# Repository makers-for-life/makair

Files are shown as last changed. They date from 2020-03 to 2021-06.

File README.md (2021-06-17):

MakAir — Covid-19 Ventilator
=====

Mass-producible open-source Covid-19 ARDS ventilator. Aims at helping hospitals cope with a possible shortage of professional ventilators during the outbreak. Worldwide.

**Makair ventilator is the world's first open-source ventilator tested with success on human patients** with ongoing clinical trials in France.

We are a distributed team of 200+ contributors (engineering, medical, regulatory, etc.), mostly spread through France. Makers, developers, university teachers, researchers and medical teams collaborated on this project. Our testing & assembly operations are located in France.

As to ensure international outreach, we made sure that contents required to build your own MakAir ventilator are available in English. The MakAir project has [a website of its own](https://makair.life/).

If you're new there, please read the explanations below. _Your contributions are much welcome!_

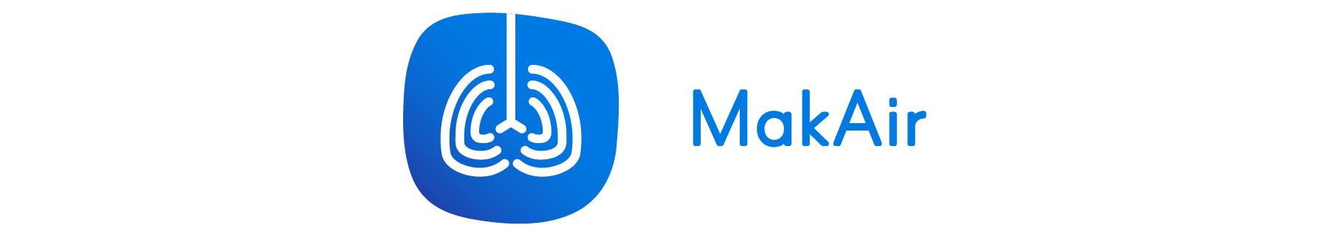
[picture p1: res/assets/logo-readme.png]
MakAir Logo


---

**Quick introduction video:**

<p align="center">
  <a href="https://www.youtube.com/watch?v=3ZcYR6X3NxE">
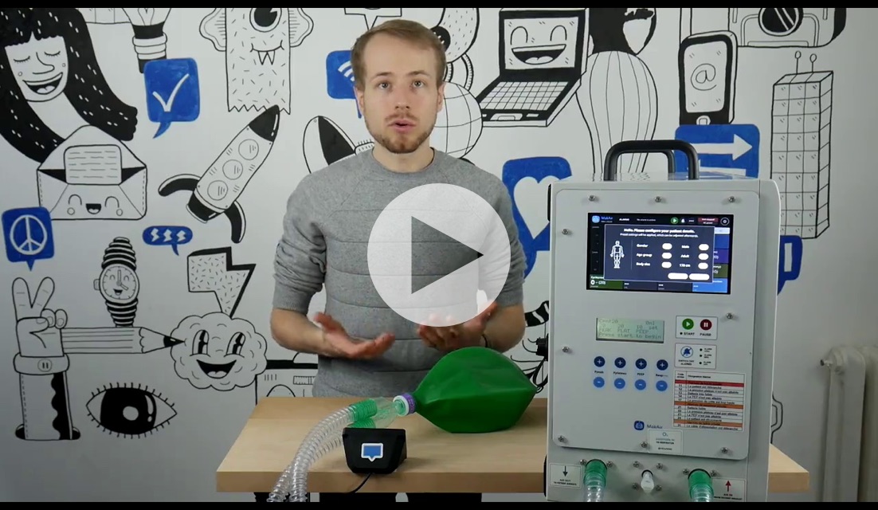
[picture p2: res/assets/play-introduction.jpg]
Play Introduction Video
    
  </a>
</p>

---

# Abstract

Roughly, the idea is as follows: as of April 2020 and due to the Covid-19 pandemic, hospitals throughout the world may start lacking mechanical artificial ventilators. We built a pump, and a valve system (controlled by electronics). This way, the breathing cycle can be enforced by proper air routing through the valve system.

Our ventilator is able to handle pressure-controlled breathing, stabilized using a [PID controller](https://en.wikipedia.org/wiki/PID_controller) in the software.

In order to ensure a proper breathing cycle (inhale + exhale), multiple valves need to be connected together to form a circuit. Their motors need to be controlled in harmony so that the air routing between each valve unit is consistent.

This project provides all the parts required to build a good-enough [ARDS](https://en.wikipedia.org/wiki/Acute_respiratory_distress_syndrome) ventilator from mass-produced components. We provide all the required mechanical parts, electronics designs & boards, and firmwares. This ventilator can be 3D-printed and ran on an Arduino board (the maker way), though we **highly advise** that you work with industrial processes as to mold medical-grade plastic parts and assemble the whole ventilator (this would be required for the built ventilator to pass all medical certifications).

We target a per-unit cost well under 500 EUR, which could easily be shrunk down to 200 EUR or even 100 EUR per ventilator given proper economies of scale, as well as choices of cheaper on-the-shelf components (eg. servomotors).

Features include:

- Pressure controlled ventilation (sedated / intubated patients)
- Volume controlled ventilation (sedated / intubated patients)
- BiPap ventilation (non sedated patients with oxygen mask)
- 4 hours battery life
- Medical-grade alarms
- High flow turbine (up to 100 L/min)
- Up to 15 L/min oxygen
- Fault tolerant design
- Designed to be used continuously and intensively during 30 days

MakAir ventilator has been tested by independent researchers and studies found that it can compare with expensive hospital reanimation ventilators (less than 5% error on target pressures and volumes).

Mechanically-speaking, the overall system is composed of sub-components that can be plugged together and wired to form an air circuit, namely:

- **Air pump** (called "Blower");
- **Air pump casing fit** (called "Blower Holder");
- **Valve system** (called "Pressure Valve");
- **Oxygen Mixer valve** (called "Oxygen Mixer");
- **Air filter casing (patient variant)** (called "Patient Filter Box");
- **Air filter casing (machine variant)** (called "Machine Filter Box"; intake + outtake);
- **Connectors** (called "Pneumatic Connectors");
- **Fan support** (called "Fan Holder");

All those components are fitted in box (ie. a casing) that we designed:

- **Housing container** (called "Casing");

---

# Designs

## MakAir Standard (Current Design)

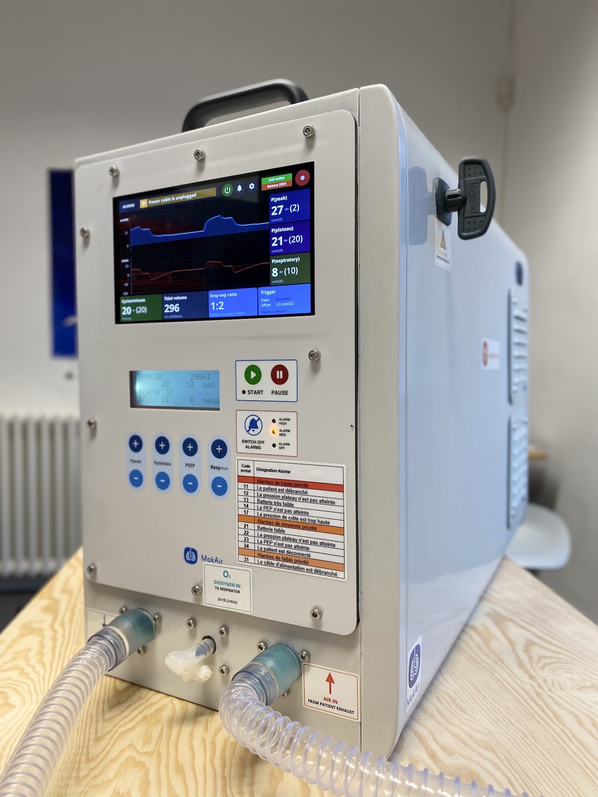
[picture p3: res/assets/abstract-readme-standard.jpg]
MakAir Standard


## MakAir Mini (Experimental Design)

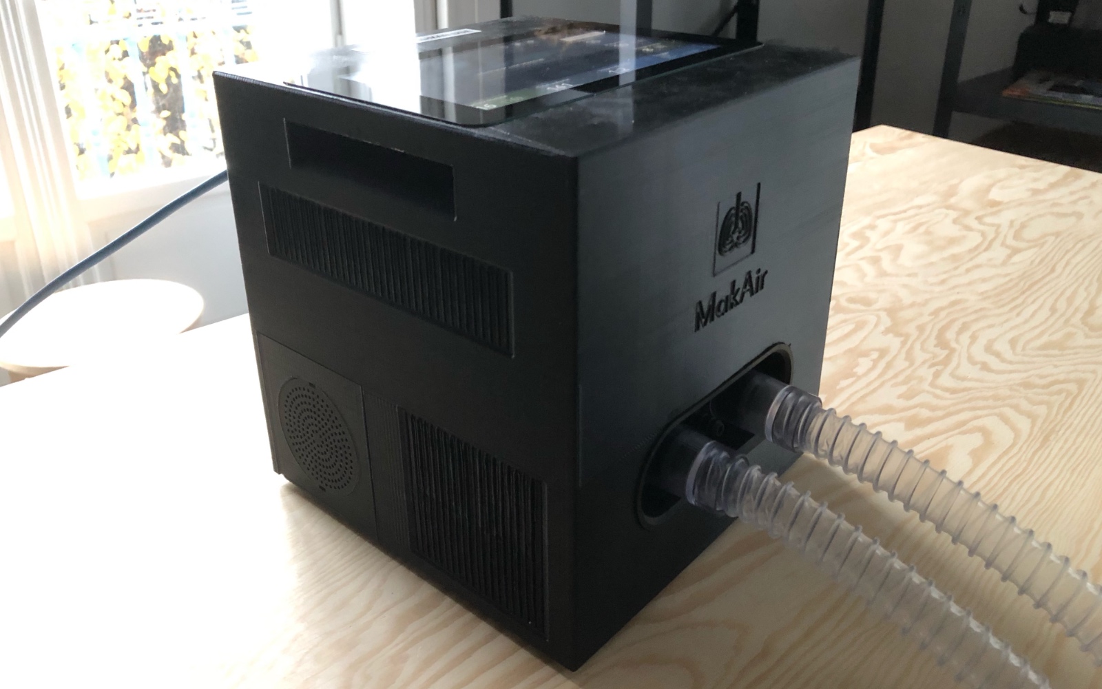
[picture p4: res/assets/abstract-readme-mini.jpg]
MakAir Mini


---

# ⚠️ Warning Notices

**A few important words before you start:**

1. Though 3D-printing (FDM and SLA) can be used to build your own ventilator — this will definitely not scale well to mass-produce MakAir ventilators, and parts might be brittle or leak air. Please work with proper industrial methods and processes if you want to build your own MakAir ventilators.

2. As ARDS patients are sedated, their breathing cycle is forced by mechanical ventilation, while they are intubated. A failing ventilator (due to bad mechanics, pneumatics or software) could kill the patient (O2 desaturation), or permanently damage their lung alveoli (overpressure). It is critical that any self-built MakAir ventilator is tested against a lung simulator system (eg. [ASL 5000](https://www.ingmarmed.com/product/asl-5000-breathing-simulator/)), and validated by medical experts.

3. Medical-grade plastic should be used to produce ventilators, and any kind of grease or adhesive chemicals must be avoided in the ventilator. The ventilators should be produced in a [cleanroom](https://en.wikipedia.org/wiki/Cleanroom) as to avoid dust & germ contaminations.

4. The pneumatic circuit should be thoroughly tested for leaks and its ability to withstand elevated positive air pressure. Joints should be used where relevant, and medical-grade flexible pipes should be used between components.

5. While the MakAir ventilators produced on-site in France were validated by a medical & engineering board, you should independantly seek validation of the MakAir ventilators that you produce; as your assembly methods or parts may vary with ours.

_MakAir and Makers For Life should not be held resposible — at any time, for harm caused to human life (eg. lung damage or loss of life). By building your own MakAir, you are held responsible for its safety validations & use._

# Projects

As the MakAir ventilator project grew up to be quite large, it is split up in sub-repositories (eg. firmware, PCB designs, etc.).

**Software:**

* **[makair-firmware](https://github.com/makers-for-life/makair-firmware)**: The firmware software source code and builds, that runs on the motherboard;
* **[makair-control-ui](https://github.com/makers-for-life/makair-control-ui)**: The control user interface, that shows realtime graphs of the ventilator while running, on a LCD display;
* **[makair-telemetry](https://github.com/makers-for-life/makair-telemetry)**: The telemetry library (and CLI tool), used as a protocol bridge between the Firmware and Control UI;

**Electronics:**

* **[makair-motherboard](https://github.com/makers-for-life/makair-motherboard)**: The motherboard electronics and PCB design;
* **[makair-boards](https://github.com/makers-for-life/makair-boards)**: Other boards PCB design (smaller control boards);

**Mechanics:**

* **[makair-parts](https://github.com/makers-for-life/makair-parts)**: The mechanical parts that can be 3D-printed and assembled to build the pneumatic circuit;
* **[makair-casing](https://github.com/makers-for-life/makair-casing)**: The MakAir casing which houses all electronics and pneumatics;

**Misc.:**

* **[makair-files](https://github.com/makers-for-life/makair-files)**: Large files, eg. the control UI system image that can be readily flashed and used;
* **[makair-simulator](https://github.com/makers-for-life/makair-simulator)**: The MakAir hardware simulator, that let us run a simulated firmware instance on a computer (for development purposes, ie. not used on ventilator units);
* **[makair-simulator-web](https://github.com/makers-for-life/makair-simulator-web)**: The Web version of the MakAir hardware simulator, that let us run a simulated firmware instance in a Web browser (for development purposes, ie. not used on ventilator units);

# How To Build?

This section aims at introducing you on how to manufacture your own MakAir — _the 3D-printed way_. In other words, we will explain there how to build a DIY MakAir using on-the-shelf parts and 3D printers.

## 1️⃣ Print all the parts

In order to 3D-print your MakAir, please first ensure you have access to a [SLS](https://en.wikipedia.org/wiki/Selective_laser_sintering) 3D printer at best (eg. [HP Multi Jet Fusion](https://www8.hp.com/us/en/printers/3d-printers/products/multi-jet-technology.html)), or otherwise a [SLA](https://en.wikipedia.org/wiki/Stereolithography) printer (eg. [Formlabs Form 3](https://formlabs.com/3d-printers/form-3/)). If you want to use a [FDM](https://en.wikipedia.org/wiki/Fused_filament_fabrication) printer (eg. [MakerBot Method](https://www.makerbot.com/3d-printers/method/)), please note that some precise parts have been optimized for SLA or SLS printing. Some parts may not print well using FDM printers, even on decent hardware.

**👉 To sum up:** at best, use a SLS metal printer, else, use a SLA resin printer. If you do not have access to either of these, you may fallback on a FDM filament printer (using [PLA](https://en.wikipedia.org/wiki/Polylactic_acid) or [ABS](https://en.wikipedia.org/wiki/Acrylonitrile_butadiene_styrene) filaments).

### 1. Parts

You can find a list of all parts that should be 3D-printed, as well as the number of parts that should be printed for each one (pick the last active version for each part):

- 1 x **Blower** — Print [all STL parts](https://github.com/makers-for-life/makair-parts/tree/master/src/blower/printing/stl) using the same printer (SLA or SLS; FDM discouraged; 50 microns minimum);
- 2 x **Pressure Valve** — Print [all STL parts](https://github.com/makers-for-life/makair-parts/tree/master/src/pressure-valve/printing/stl) using the same printer (SLA, SLS or FDM; 200 microns minimum);
- 1 x **Oxygen Mixer** — Print [the STL part](https://github.com/makers-for-life/makair-parts/tree/master/src/oxygen-mixer/printing/stl) (SLA or SLS; FDM discouraged; 100 microns minimum);
- 1 x **Patient Filter Box** — Print [all STL parts](https://github.com/makers-for-life/makair-parts/tree/master/src/patient-filter-box/printing/stl) using the same printer (SLA, SLS or FDM; 100 microns minimum);
- 1 x **Machine Filter Box (Intake)** — Print [all STL parts](https://github.com/makers-for-life/makair-parts/tree/master/src/machine-filter-box/printing/stl) using the same printer, make sure that you pick the proper sub-part (SLA or SLS; FDM discouraged; 100 microns minimum);
- 1 x **Machine Filter Box (Outtake)** — Print [all STL parts](https://github.com/makers-for-life/makair-parts/tree/master/src/machine-filter-box/printing/stl) using the same printer, make sure that you pick the proper sub-part (SLA or SLS; FDM discouraged; 100 microns minimum);
- 1 x **Pneumatic Connectors (Blower)** — Print [the STL part](https://github.com/makers-for-life/makair-parts/tree/master/src/pneumatic-connectors/printing/stl) using the same printer, make sure that you pick the proper sub-part (SLA or SLS; FDM discouraged; 100 microns minimum);
- 1 x **Pneumatic Connectors (O2)** — Print [the STL part](https://github.com/makers-for-life/makair-parts/tree/master/src/pneumatic-connectors/printing/stl) using the same printer, make sure that you pick the proper sub-part (SLA or SLS; FDM discouraged; 100 microns minimum);
- 1 x **Pneumatic Connectors (No Pressure)** — Print [the STL part](https://github.com/makers-for-life/makair-parts/tree/master/src/pneumatic-connectors/printing/stl) using the same printer, make sure that you pick the proper sub-part (SLA or SLS; FDM discouraged; 100 microns minimum);
- 1 x **Pneumatic Connectors (Pressure)** — Print [the STL part](https://github.com/makers-for-life/makair-parts/tree/master/src/pneumatic-connectors/printing/stl) using the same printer, make sure that you pick the proper sub-part (SLA or SLS; FDM discouraged; 100 microns minimum);

If you are using your own proprietary blower — _in addition to the parts above_ — please adjust the [Blower Holder](https://github.com/makers-for-life/makair-parts/tree/master/src/blower-holder) CAD model and print it as well (this one prints well using a FDM printer at worst).

### 2. Casing

Now that you got all parts printed, you may assemble them in the MakAir casing box. We recommend that you build the casing using laser-cut acrylic panels. You may find the casing CAD model for [Fusion 360](https://github.com/makers-for-life/makair-casing/tree/master/src/fusion) or as a [STEP file](https://github.com/makers-for-life/makair-casing/tree/master/src/step).

_Please ensure that you cut your acrylic panels using the same sizes than stated on our models; as those sizes are optimized to contain all required parts and electronics in the minimum amount of space._

## 2️⃣ Setup the electronics

Electronics are comprised of two parts: the firmware controller board (typically, an Arduino), and the "raw" PCB electronics (LCD, interface buttons, alarm beeper, etc.). Those parts make up the motherboard, on the top of which a rigid panel is mounted, and user instructions are printed (eg. control button bindings).

### 1. Motherboard

The motherboard electronic schematics and wiring diagrams [can be found there](https://github.com/makers-for-life/makair-motherboard/tree/master/src/schematics). Please pick the last version available.

👋 _If you need help on this step, you may [open an issue](https://github.com/makers-for-life/makair-motherboard/issues/new)._

### 2. Smaller Boards

The smaller boards electronic schematics and wiring diagrams [can be found there](https://github.com/makers-for-life/makair-boards/tree/master/src/schematics). Please pick the last version available. Those boards are used eg. to control the pinch valve motor or Raspberry Pi hardware clock.

👋 _If you need help on this step, you may [open an issue](https://github.com/makers-for-life/makair-boards/issues/new)._

### 3. Control Unit Screen

The control unit is made of a [Raspberry Pi 4](https://www.raspberrypi.org/products/raspberry-pi-4-model-b/) computer, plugged to a [Raspberry Pi Touch Display](https://www.raspberrypi.org/products/raspberry-pi-touch-display/).

👋 _If you need help on this step, you may [open an issue](https://github.com/makers-for-life/makair-control-ui/issues/new)._

## 3️⃣ Flash the firmware

### 1. Ventilator Firmware

Now that both mechanical parts and electronics are ready, you may flash the latest MakAir firmware binary on your firmware controller board (Arduino, ST Nucleo, or other).

Firmware release binaries are available for download on our [releases page](https://github.com/makers-for-life/makair-firmware/releases).

👋 _If you need help on this step, you may [open an issue](https://github.com/makers-for-life/makair-firmware/issues/new)._

### 2. Control Unit Runtime

The Control Unit should be built and ran on the Raspberry Pi 4 using instructions available on the [Control Unit](https://github.com/makers-for-life/makair-control-ui) documentation. You should flash the system image readily available in the [Files](https://github.com/makers-for-life/makair-files) repository.

👋 _If you need help on this step, you may [open an issue](https://github.com/makers-for-life/makair-control-ui/issues/new)._

# Schemes

## Pneumatic Circuit Scheme

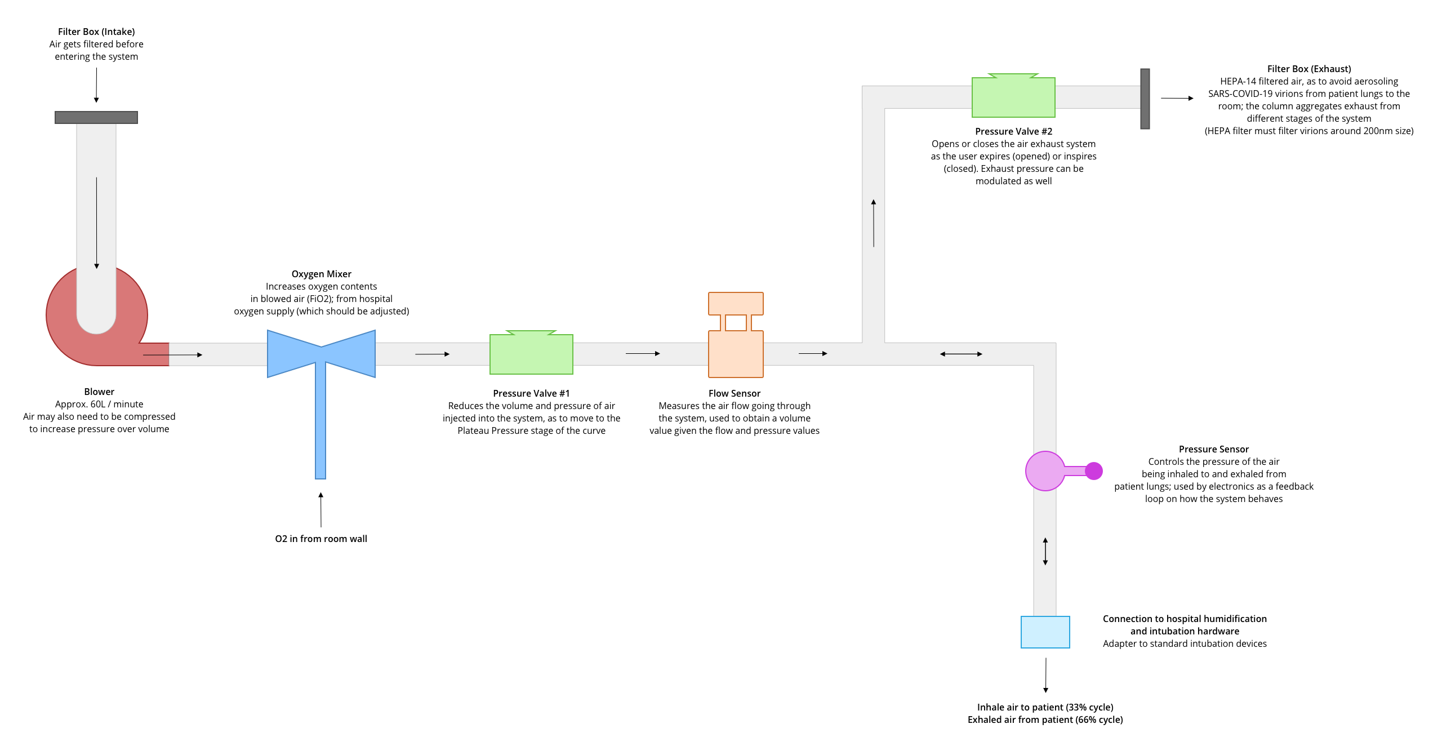
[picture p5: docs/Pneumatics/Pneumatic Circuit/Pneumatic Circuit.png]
Pneumatic Circuit Scheme


_(design by [Valerian Saliou](https://github.com/valeriansaliou))_

## Casing Layout

### Top Part: Electronics (Power & Controllers)

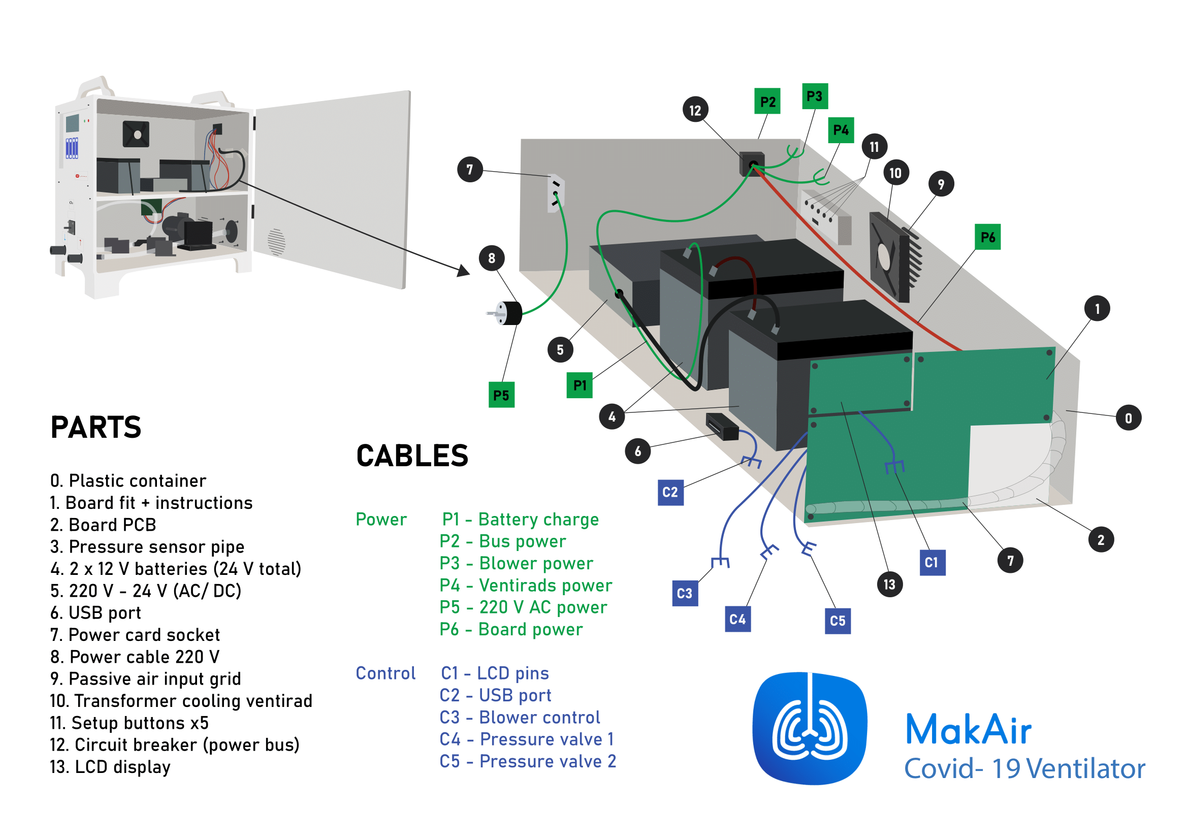
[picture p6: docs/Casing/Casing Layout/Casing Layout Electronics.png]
Casing Layout Electronics Drawing


_(design by Arthur Dagard; drawing by [Valerian Saliou](https://github.com/valeriansaliou); remake by [Lāsma Fedotova](https://github.com/lasmafedotova))_

### Bottom Part: Pneumatics

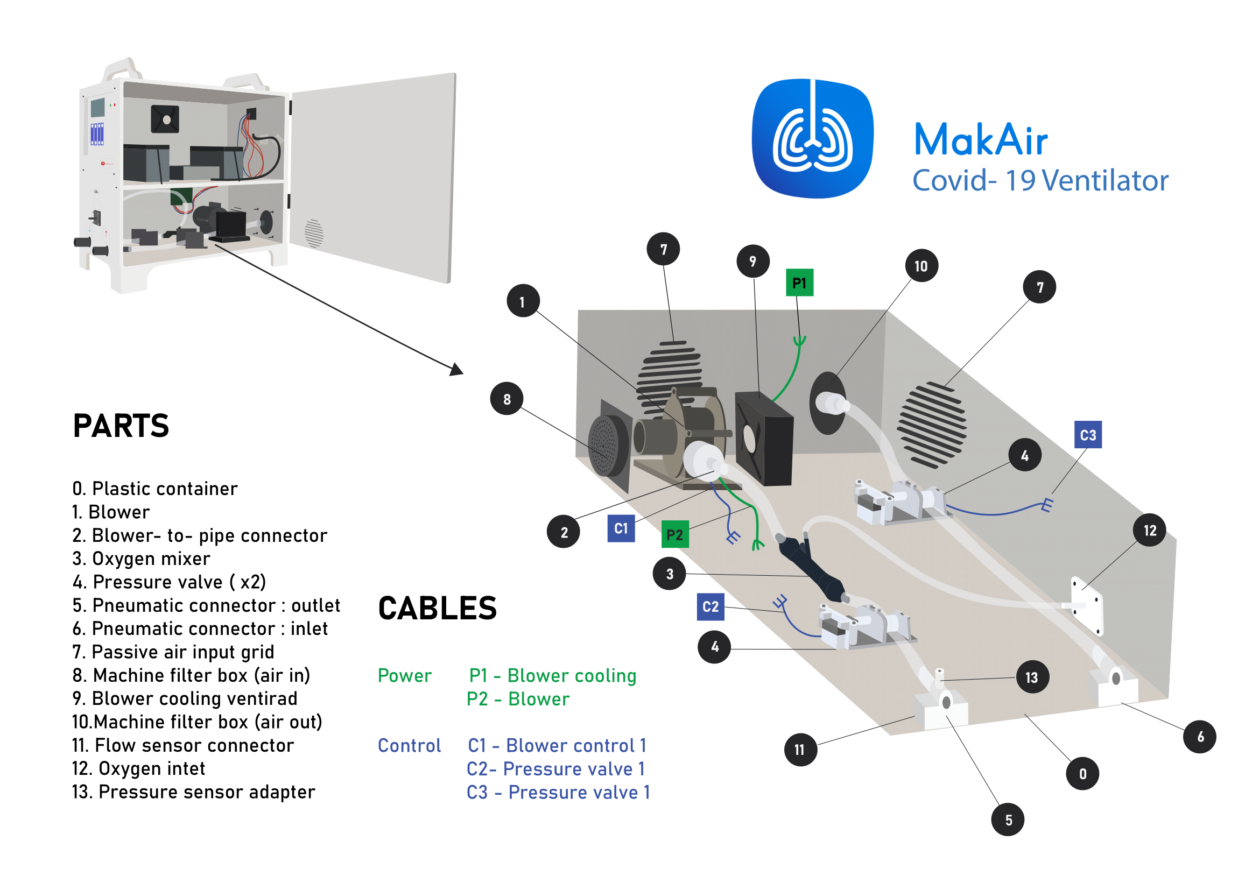
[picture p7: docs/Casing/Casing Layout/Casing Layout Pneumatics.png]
Casing Layout Pneumatics Drawing


_(design by Arthur Dagard; drawing by [Valerian Saliou](https://github.com/valeriansaliou); remake by [Lāsma Fedotova](https://github.com/lasmafedotova))_

# Article Series

A series of explanatory articles have been written on the MakAir story, with the goal of making it easier for teams in the future to start their own ventilator project:

* 1️⃣ [MakAir Series: The Inception of an Open-Source Ventilator Project](https://journal.valeriansaliou.name/makair-series-the-inception-of-an-open-source-ventilator-project/)
* 2️⃣ [MakAir Series: How to Ventilate a Human Patient 101](https://journal.valeriansaliou.name/makair-series-how-to-ventilate-a-human-patient-101/)
* 3️⃣ [MakAir Series: The Building Blocks of a Mechanical Ventilator](https://journal.valeriansaliou.name/makair-series-the-building-blocks-of-a-mechanical-ventilator/)
* 4️⃣ [MakAir Series: Engineering Focus on Ventilator Pneumatics](https://journal.valeriansaliou.name/makair-series-engineering-focus-on-ventilator-pneumatics/)
* 5️⃣ [MakAir Series: Engineering Focus on Ventilator Electronics](https://journal.valeriansaliou.name/makair-series-engineering-focus-on-ventilator-electronics/)
* 6️⃣ [MakAir Series: Engineering Focus on Ventilator Software](https://journal.valeriansaliou.name/makair-series-engineering-focus-on-ventilator-software/)

# News & Contact

## Updates

* Live updates on Telegram: [join "Newsroom MakAir (Covid-19 Ventilator)"](https://t.me/joinchat/AAAAAE_99-k7pKZur-GXCQ)
* YouTube channel: [view "MakAir" on YouTube](https://www.youtube.com/channel/UCcf_3KXjeJSMz39J6gsyTSg)
* Coordination on Slack: [request to join "Makers For Life"](https://github.com/makers-for-life/makair/issues/new) (open an issue)

## Contacts

* Open-source & questions: [please open an issue on GitHub](https://github.com/makers-for-life/makair/issues/new)
* Press contacts: [Grégory Thibord](https://twitter.com/thibord) ([email](mailto:gregory.thibord@lepalace.work))
* Medical contacts: [Pierre Antoine Gourraud](http://www.itun.nantes.inserm.fr/Team-5/Pierre-Antoine-Gourraud) ([email](mailto:pierre-antoine.gourraud@univ-nantes.fr))
* Industry relations: [Quentin Adam](http://waxzce.org/) ([email](mailto:quentin.adam@clever-cloud.com))
* Engineering contact (mechanics): [Valerian Saliou](https://valeriansaliou.name/) ([email](mailto:valerian@valeriansaliou.name))
* Engineering contact (software): [David Sferruzza](https://david.sferruzza.fr/) ([email](mailto:david.sferruzza@gmail.com))
* Engineering contact (electronics): Vincent Le Cunff ([email](mailto:v.lecunf@gmail.com))

# Sponsors & Contributors

This project would not have been possible without the support of those companies and organizations, which have put human, real estate and/or financial resources at work on the project:

* [Clever Cloud](https://www.clever-cloud.com/) (founding team)
* [Crisp](https://crisp.chat/) (founding team)
* [Cooprint](https://cooprint.fr/) (CAD)
* [SenX](https://senx.io/) (electronics)
* [Tronico](https://www.tronico-alcen.com/) (PCB design)
* [Renault Group](https://www.renault.fr/) (manufacturing)
* [SEB Group](https://www.groupeseb.com/) (manufacturing)
* [Le Palace Nantes](https://lepalace.work/) (team offices)
* [Parrot](https://www.parrot.com/) (hardware provider)
* [STMicroelectronics](https://www.st.com/) (hardware provider)
* [Diabeloop](https://www.diabeloop.com/) (regulatory help)
* [Legrand](https://www.legrand.fr/) (hardware provider)
* [RTsys](https://rtsys.eu/) (engineering provider)

We are supported by public entities as well, namely:

* [Defence Innovation Agency](https://www.defense.gouv.fr/) (Ministry of Armed Forces of France)
* [CEA](http://www.cea.fr/) (France)
* [CHU of Nantes](https://www.chu-nantes.fr/) (France)
* [University of Nantes](https://www.univ-nantes.fr/) (France)
* [City of Nantes](https://metropole.nantes.fr/) (France)
* [Region of Auvergne-Rhône-Alpes](https://www.auvergnerhonealpes.fr/) (France)

Adding to that, 200+ individual members of the project who contributed to technical, legal, medical and press subjects (and more).

# Research Papers

* [Can Open Source Hardware Mechanical Ventilator initiatives help cope with the COVID-19 health crisis](https://www.sciencedirect.com/science/article/pii/S2468067220300596) (English)
* [MakAir, a COVID-19-born ventilation machine, combining 3D printing design, digital control and open innovation](https://www.sciencedirect.com/science/article/pii/S1279847920301129) (French)

# Press Coverage

## 📺 TV

* [France 3, 21st April 2020](https://www.youtube.com/watch?v=M3QLCvUyIII) (French-speaking)
* [TF1, 26th April 2020](https://www.youtube.com/watch?v=2X157RLbRIA) (French-speaking)

## 🗞 Newspapers

* [Makery, 23th July 2020](https://www.makery.info/en/2020/07/23/quentin-adam-lopen-source-medical-est-une-idee-qui-fera-son-chemin/) (English)
* [Le Monde, 20th April 2020](https://www.lemonde.fr/campus/article/2020/04/20/entre-nantes-et-grenoble-une-course-contre-la-montre-pour-creer-un-respirateur-artificiel-a-bas-cout_6037140_4401467.html) (French-speaking)
* [Le Parisien, 21st April 2020](http://www.leparisien.fr/economie/business/coronavirus-une-equipe-nantaise-a-reinvente-le-respirateur-artificiel-en-un-mois-21-04-2020-8303016.php) (French-speaking)
* [Le Figaro, 26th April 2020](https://www.lefigaro.fr/secteur/high-tech/creer-un-respirateur-artificiel-a-bas-cout-la-folle-aventure-de-makers-for-life-20200426) (French-speaking)
* [Le Point, 6th May 2020](https://www.lepoint.fr/sciences-nature/a-brest-on-teste-le-respirateur-concu-par-des-geeks-06-05-2020-2374359_1924.php) (French-speaking)

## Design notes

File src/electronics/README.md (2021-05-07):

# Electronics

| Electronics | Repository |
| --- | --- |
| Motherboard | [makair-motherboard](https://github.com/makers-for-life/makair-motherboard) |
| Boards | [makair-boards](https://github.com/makers-for-life/makair-boards) |

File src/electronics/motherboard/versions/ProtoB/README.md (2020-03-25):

# Proto B

2020/03/25

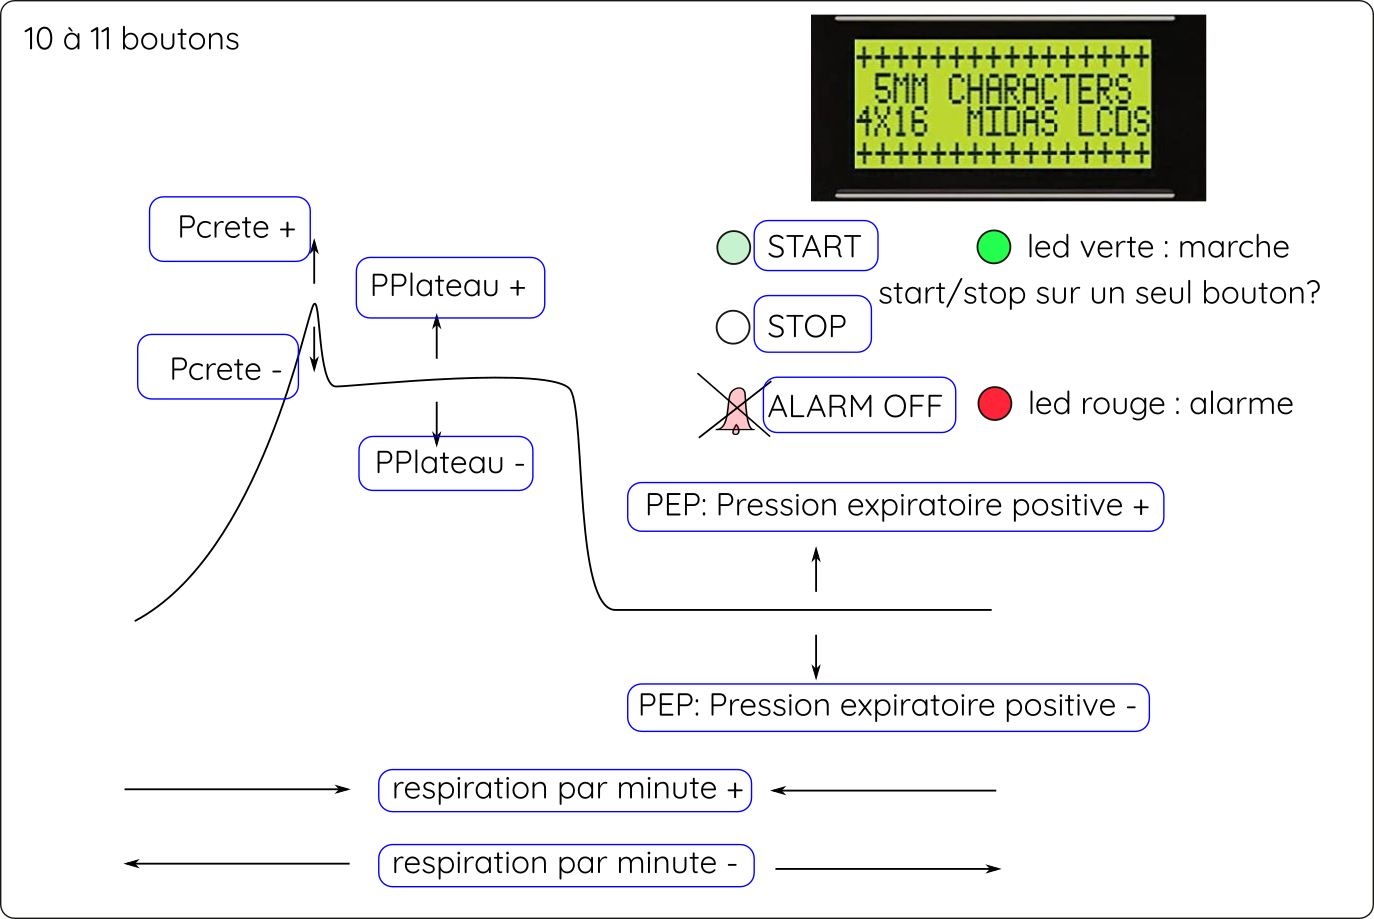
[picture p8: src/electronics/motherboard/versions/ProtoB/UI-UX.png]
ux protoB


## Requirements

- simpler calibration process: no amplification.
- only one 12V input : allow battery
- low noise : clean separation of power supply of the sensor, no ground loops, use of external ADC reference.
- able to drive the blower
- powerfull alarm buzzer
- no surface mount components
- components available and in stock in both Farnell and Radiospares.
- safety: not mandatory to have 60601, 60950-1 is enough

MHRA specifications: [link](https://assets.publishing.service.gov.uk/government/uploads/system/uploads/attachment_data/file/874279/RMVS001_Rapidly_Manufactured_Ventilator_Specification__PDF.pdf). 

## Schematic

See [pdf file](./covid-respirator-ProtoB.pdf)

## Bill Of Material

### Power supply

13.8v output to ensure a slow floating charge of a 12V lead battery:
- RS: 740-5001
- RS: 161-8267  (10A version, dangerous for battery)

### Battery
Lead battery, 7Ah.
- RS: 537-5488

### Fuse
A 7Ah 12V lead battery has enough power to harm anyone. A fuse is necessary.
10A value needs to be confirmed after blower motor will be choosen.

10A (slow fuse).
- RS: 563-429

### Fuse holder:
- RS  344-5642
- Farnell 1154859

### Sensor: 

Medical specification : `Plateau pressure should be adjusted to achieve volume and be limited
to 35 cmH2O by default. It is acceptable if an option to increase this to
70 cmH2O in exceptional circumstances is provided`
> The 1psi (69mbar, 7kPa, 703mmH2O, 27inchH2O) range is perfect.

See this comparison table of different sensors with availability around major suppliers : [google doc link](https://docs.google.com/spreadsheets/d/1qR-S2XOJmOITaHZXnXCGtpi7E2upIdV9PGvASUbvRIo/edit?usp=sharing)

[MPXV5010DP](https://www.nxp.com/docs/en/data-sheet/MPX5010.pdf) : Good range, 5% accuracy (not so good), **available for mass production**. Easy to read analog output.

[NXP MPX5010DP](https://www.nxp.com/docs/en/data-sheet/MPX5010.pdf) : Not a very good accuracy, easy to read analog output.
- RS: 719-1080
- Farnell: 1555605

[Honeywell HSCSAAN001PDAA5](https://sensing.honeywell.com/honeywell-sensing-trustability-hsc-series-high-accuracy-board-mount-pressure-sensors-50099148-a-en.pdf) : Best one. Accurate, easy to read analog output. **But only available on Farnell**.
- Farnell : 1823226

### Power Supply:
Battery size will be choosen once the blower will choosen. Any 12V lead battery can do the job, ~5Ah minimum. 

### Mains supply:
This is a battery charger. It must be able to charge the battery and keep it floating at around 13.6Volts. A good 13.8 V fixed power supply can do the job.

### Blower driver:
Arduino can drive the blower through a robust low side mosfet :

VNP35N07-E
- RS: 809-1310
- Farnell : 1739428

Blower motor may be a RC motor controlled by the arduino. **TO BE DEFINED**.

### Battery voltage feedback:
The arduino is able to monitor battery voltage and raise alarm if the voltage goes under 12.7V (mains loss). This is a simple voltage divider.

### Arduino and servo power supply:
Buck regulator that can support a wide input range:
- RS: 144-6290
- Farnell : 2760747
This could be replaced by another one easily (5V 1A output)

### Buzzer:
Powerfull Buzzer, fixed tone, electronics integrated. Just need to power it, directly with 12V supply. BC548 can be replaced by any NPN transistor that support 30V/100mA.

KXG1212CL
- RS: 771-6960
- Farnell : 2215083

BC548
- RS : 796-9713
- Farnell : 2453793

Note : R6 may be connected to +12V to power the alarm if the arduino fails. Monitoring Arduino with an external watchdog need to be discussed in ProtoC.

### Sensor supply:
In order to minimize the measure noise, the sensor has a dedicated linear regulator (7805), a bit of power filtering, a little low pass filter (R5 C4).

> The ground must come from the arduino, not from other part of the circuit.

> The sensor circuit board and power supply must be isolated from other components, and really close to the arduino. Ideally, less than 4cm of 1mm² wire.

L7805CV-DG
- RS: 793-1346
- Farnell: 2849718
47uF/25V
- RS 807-3324 
- Farnell 2917904
10uF/16V
- RS 862-3083 
- Farnell 9451692
100nF/50V
- RS 133-5716 
- Farnell 2507749

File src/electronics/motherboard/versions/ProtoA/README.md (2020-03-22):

# Proto A

2020/03/20

Sensor : MPX10GP

*-> Not the best one.*
Low accuracy, differential output that needs an amplification behind

Fritzing schematic + schematic below for amplification

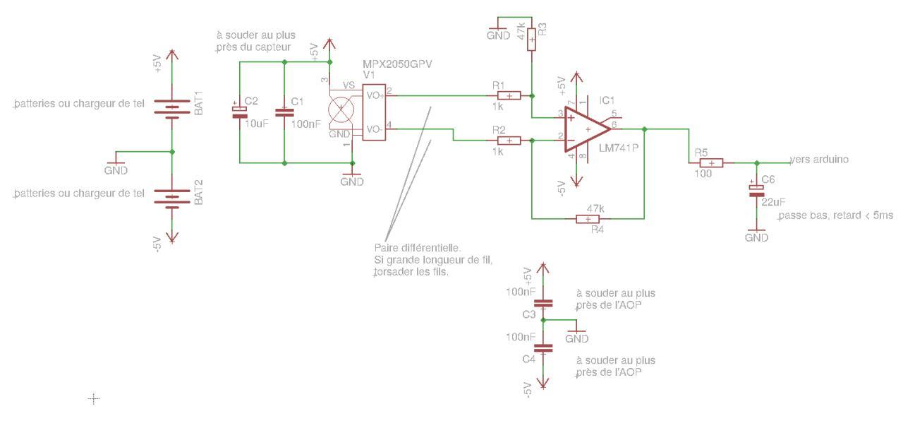
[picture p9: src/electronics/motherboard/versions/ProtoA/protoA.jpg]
ProtoA scheme


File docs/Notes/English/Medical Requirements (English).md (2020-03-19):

Medical Requirements
===

We build a respirator adapted to Severe Acute Respiratory Syndrome (rigid lungs that induce a lack of body oxygenation).

**This document sums up our specifications:**

* Mechanical invasive ventilation (medical tube to the lungs; no mask)
* Open circuit (filtering air exhaust is possible)
* An inspiratory pressure that allows to a low normal air volume (6mL/kg/min, with a possibility to push this value to 8), which gives a volume ranging from 300 to 600ml per inspiration)
* A PEEP (Positive end-expiratory pressure) that we should be able to configure from 5 to 15 cmH2O
* A respiratory frequency that must be configured between 15 to 35 per minute
* An inspiration/expiration factor of 1:2
* An intake to allow regular air to be mixed with pure oxygen (before the blower, to increase the air oxygen content on demand)
* A sensor able to measure the plateau pressure, which is allowed up to a maximum of 30cmH2O

**Features:**

* We design a controlled pressure system (in opposition to a controlled volume system)
* The system will display the plateau pressure (and possibly, the peak pressure)
* The medical personnel shall be able to tune the following parameters: PEEP, volume, frequency

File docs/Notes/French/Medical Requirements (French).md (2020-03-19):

Requis médicaux
===

Un respirateur adapté à la ventilation des SDRA (poumons rigides avec manque important d’oxygène).

**Ce document reprend nos spécifications :**

* Ventilation mécanique invasive (sonde)
* Circuit ouvert (possibiliter de filtre)
* Une Pression inspiratoire permettant d’obtenir un faible volume courant (6mL/kg/min) (possible à pousser à 8) (ce qui donne un volumme compris entre 300 et 600ml par inspiration)
* Une PEP qui doit être réglable entre 5 et 15 cmH2O (pression d"expiration positive)
* Une fréquence respiratoire qui doit être réglable entre 15 et 35/min
* Un rapport inspiration/expiration de 1:2
* Une entrée pour apporter de l’oxygène (avant blower, pouvoir passer en de 0% à 100% oxygene)
* Et un capteur qui permette de mesurer la pression de plateau qui doit être maximum à 30cmH2O

**Fonctions :**

* Nous designons un appareil à pression controlée (par opposition à un appareil à volume contrôlé)
* Affichage obligatoire de la pression de plateau (et éventuellement de créte)
* Paramètres accessibles au praticien : PEP, Volume et Fréquence

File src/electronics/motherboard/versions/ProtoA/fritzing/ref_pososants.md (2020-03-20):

http://www.farnell.com/datasheets/2291653.pdf?_ga=2.112373575.2103761512.1584720895-1819555675.1584720895

MPX10GP CASE 344B-01

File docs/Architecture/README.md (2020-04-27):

MakAir — System Architecture
=====

**This design aims to explain how MakAir has been designed and to design new features thanks to a consistent architecture sketch.**

A system architecture model provides this two main goals:
- a functional analysis to explain what funtion each part has to perform
- an architecture schema to explain how each parts of MakAir interacts with the others

By providing a visual system view of Makair, it become easier to ramp up on the project as contributors can have an overview of the system without going to deeply in implementation considerations (like electronics, software, mechanic). A diagram can be easier to read than long document. For certification and validation, it can also be helpful as it provides a proof of consistency between Hardware, Software and Specifications.

# How to read this model?

This architecture design has been created with the Open Source project: [Capella](https://www.eclipse.org/capella). This project used a simple methodolody named [Arcadia](https://www.eclipse.org/capella/arcadia.html) to guide users accross each steps. In a nutshell:
- Operational: how users (patient, doctors, external system) interacts with together
- System: the Airmake as a black box, with a the function it is suppose to perform and interface with others systems
- Logical: the Airmake as a white box, with its internal subcomponents but without implementation details
- Physic: allocation of logical functions and components to the hardware and software

There is a full traceability from a step to the other one, to track how an initial requirement has been satisfied in a subpart of MakAir.

Is it too complex for me? For information, this project has been started by a 9 year old child. So, after 5 min, you can understand it.

# Authors

- Marceau Juliot (9 yo)
- Léonie Juliot (14 yo)
- [Etienne Juliot](https://github.com/ejuliot)

Special thanks to [Frederic Madiot](https://github.com/fmadiot) for this idea of contribution.

It is a draft document. Any contribution is welcomed.

## How to contribute?

Download Capella 1.4 at https://www.eclipse.org/capella/download.html then import this project.
Use Github to propose an update.

# Operational Analysis

Who are the actors?
<p>
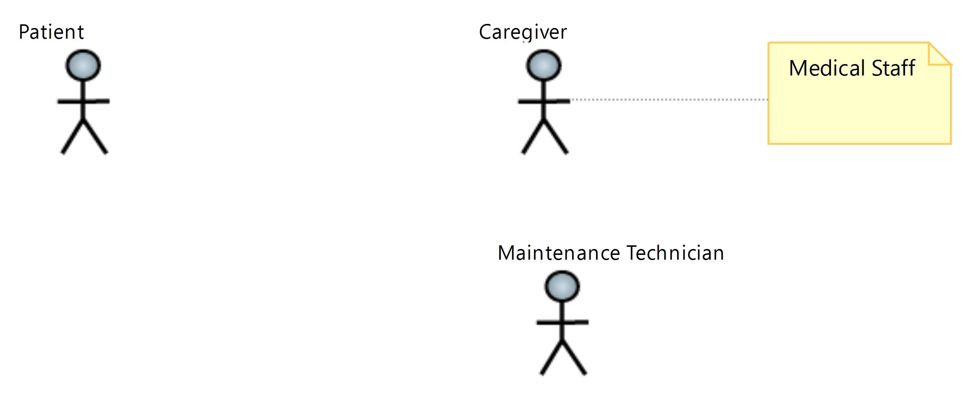
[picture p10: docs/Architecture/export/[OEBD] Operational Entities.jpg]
  
</p>

Which activities do they perform?
<p>
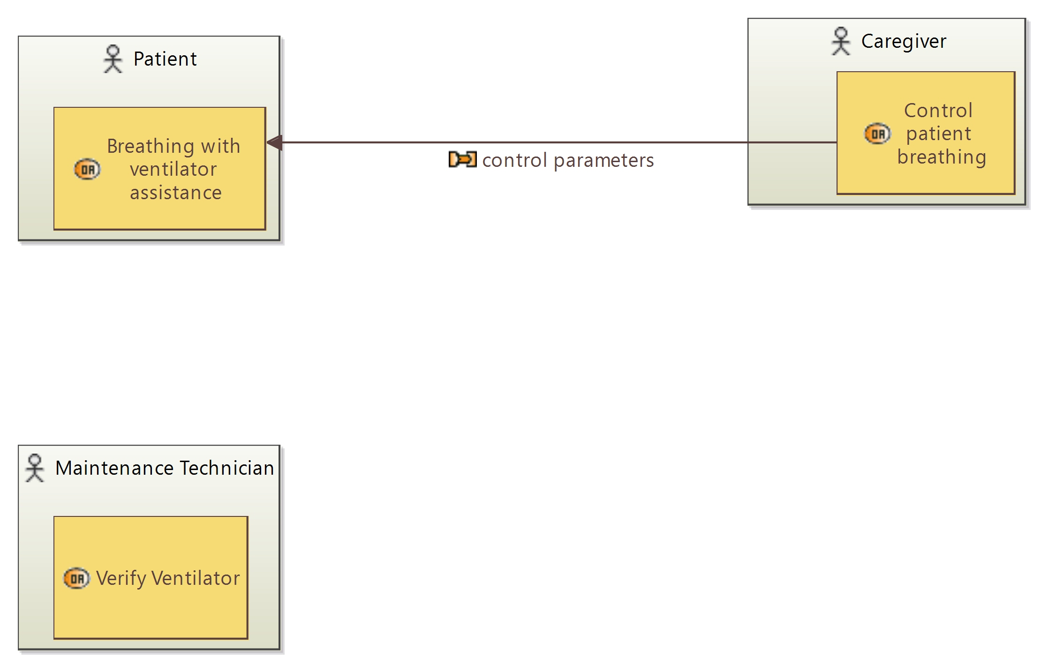
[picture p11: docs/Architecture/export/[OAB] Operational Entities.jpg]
  
</p>

## Comments

- Does the maintenace Technician has really a role? If yes, what he can really peform with MakAir?

# System Analysis

Which main functions does MakAir perform? And does a function need other functions to work (provided by MakAir or an another system provided by the hospital)?
<p>
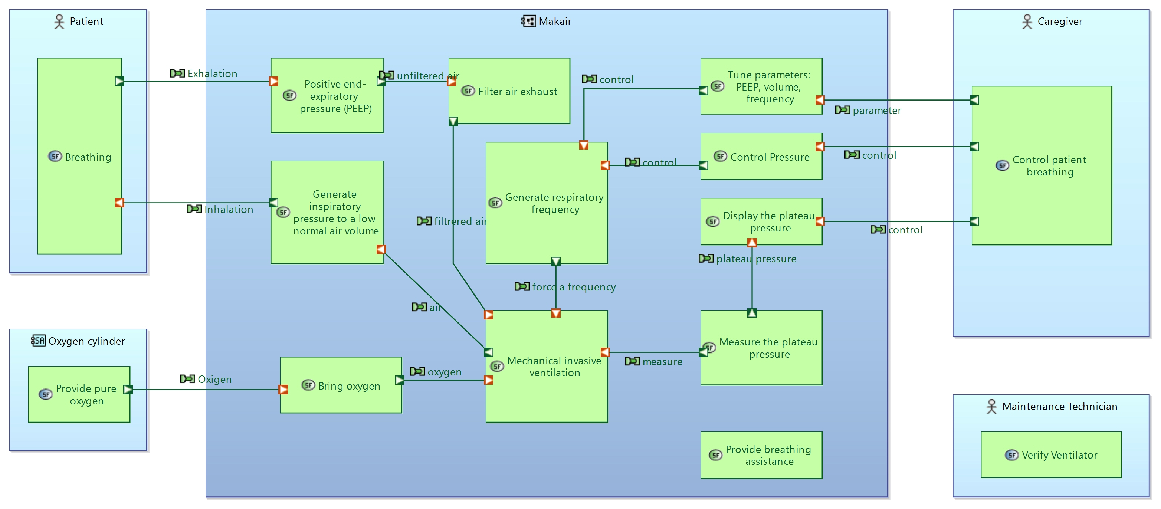
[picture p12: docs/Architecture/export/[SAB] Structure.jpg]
  
</p>

This analysis has been performed thanks to [these requirements](https://github.com/makers-for-life/makair/blob/master/docs/Notes/English/Medical%20Requirements%20(English).md).

# Logical Architecture

How the internal of MakAir is organized, in term of subcomponents? What are the functions performed by each subcomponent?
<p>
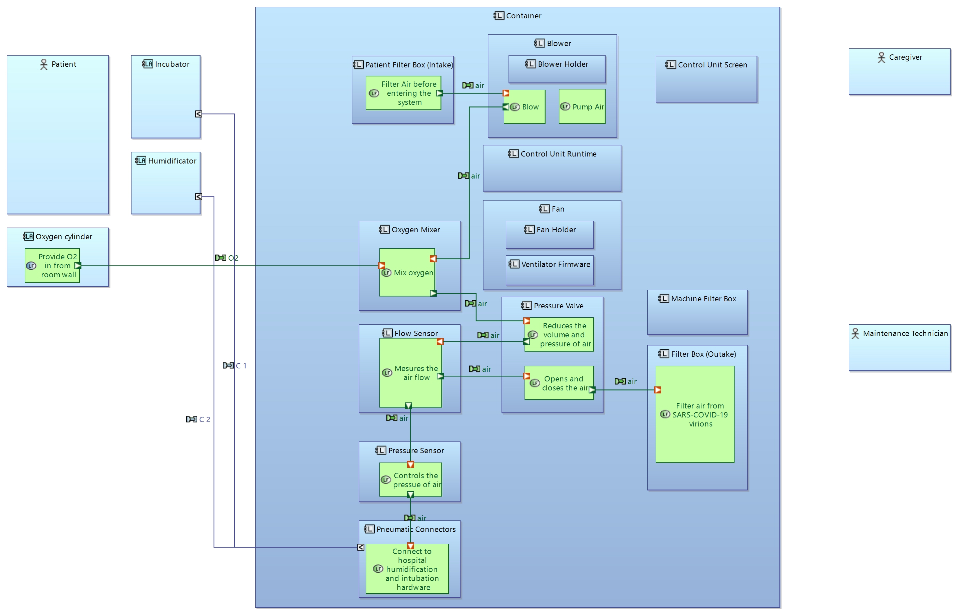
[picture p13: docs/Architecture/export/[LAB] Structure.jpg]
  
</p>

What is the functional dataflow of the pneumatic circuit?
<p>
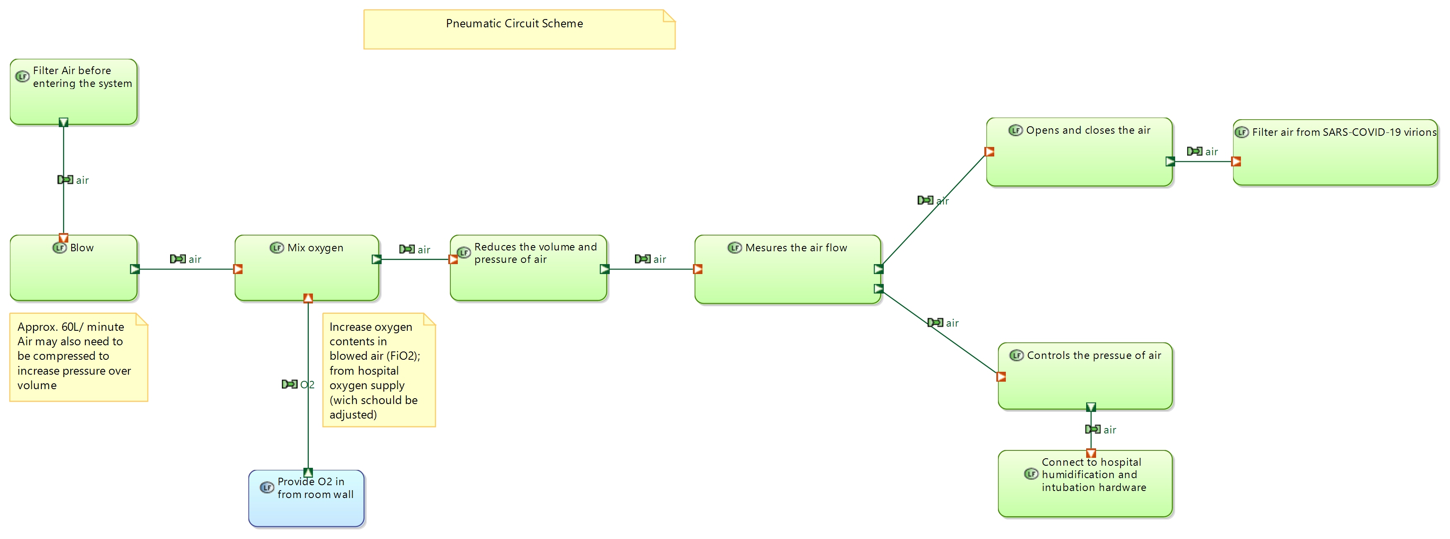
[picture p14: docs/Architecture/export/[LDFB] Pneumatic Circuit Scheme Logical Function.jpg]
  
</p>

## Comments

- It should be useful to add functions relative to software algorithms.

# Physical Architecture

What is the physical breakdown of MakAir, to identify each physical part?
<p>
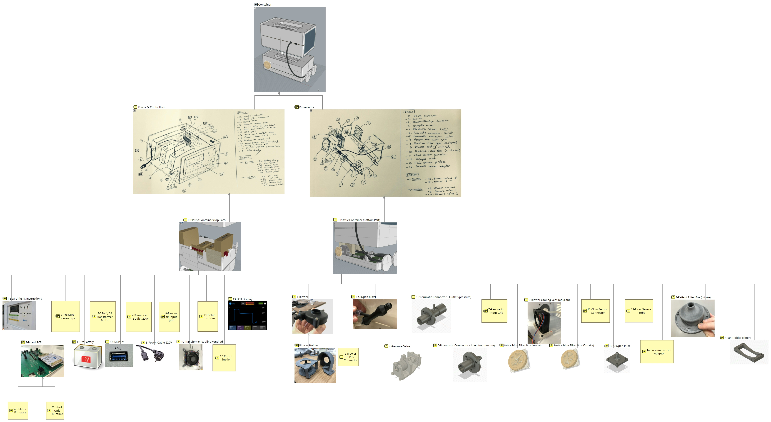
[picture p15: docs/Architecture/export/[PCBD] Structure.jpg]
  
</p>

How each physical part are deployed in the container and how are they connected together?
<p>
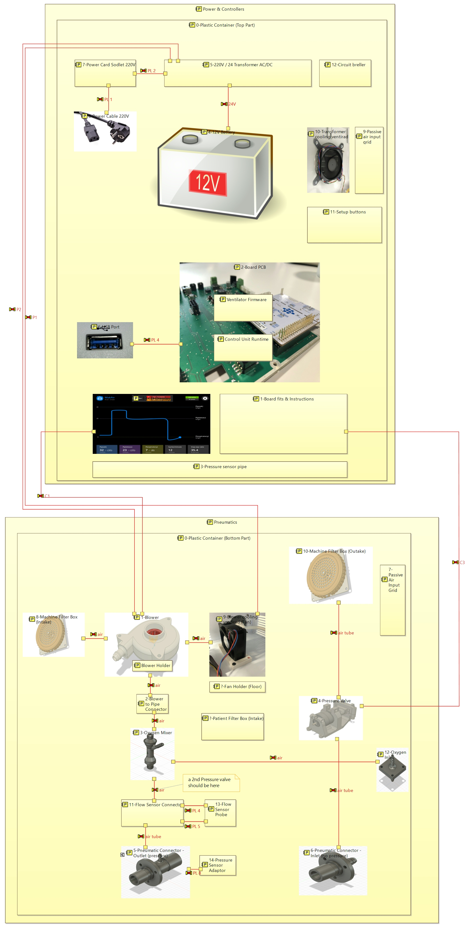
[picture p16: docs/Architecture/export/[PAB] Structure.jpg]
  
</p>

## Comments

- It should be useful to add implementation choice relative to software (deployment units)
- It should be useful to create diagrams which show how logical components and their functions are deployed on physical components.

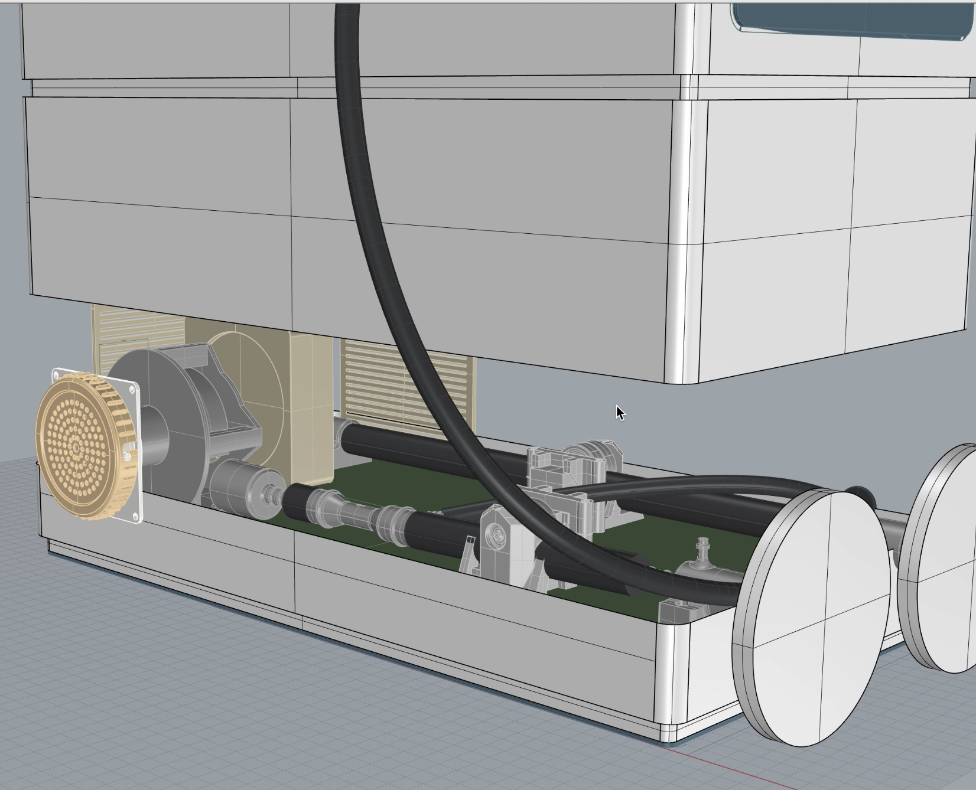
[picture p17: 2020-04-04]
docs/Architecture/pictures/Container (Render 8).png

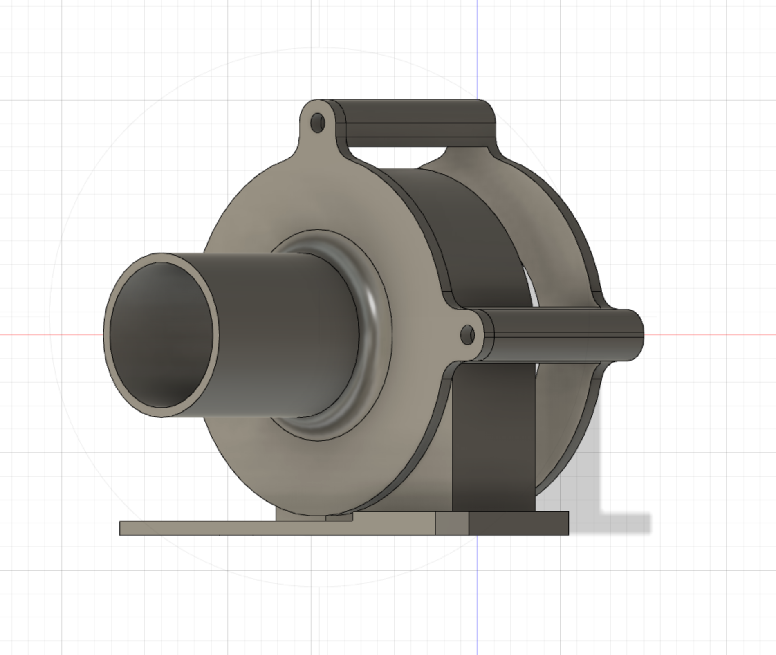
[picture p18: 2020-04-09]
docs/Architecture/pictures/Blower Holder Model A (Render 1).png

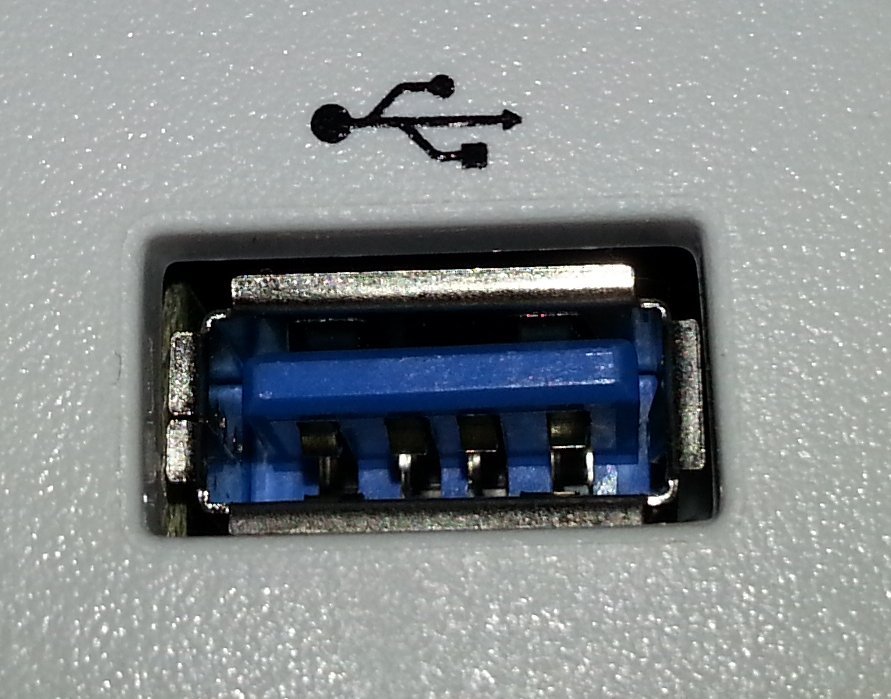
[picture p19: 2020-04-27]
docs/Architecture/pictures/Blue_USB_port_without_USB_3.0_contacts.jpg

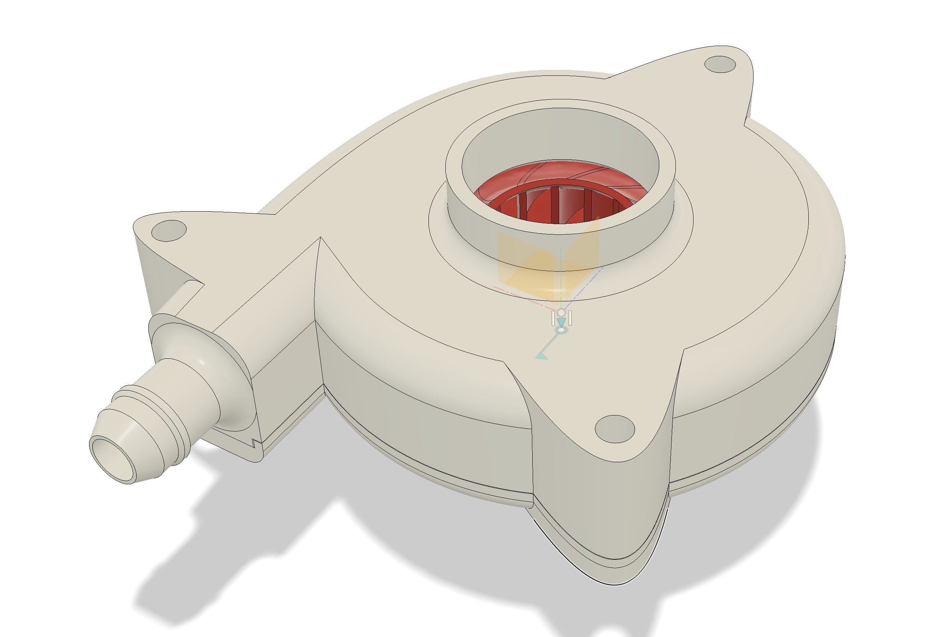
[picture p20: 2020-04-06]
docs/Architecture/pictures/Blower (Render 1).png

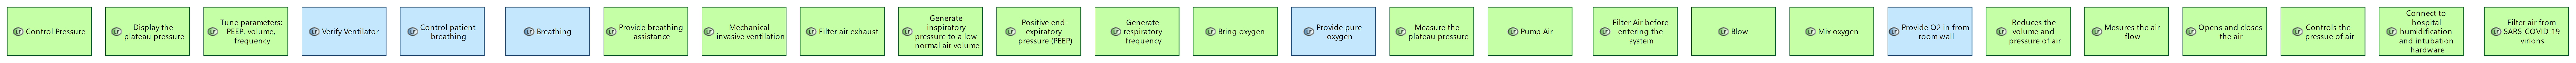
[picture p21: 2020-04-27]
docs/Architecture/export/[LFBD] Root Logical Function.jpg

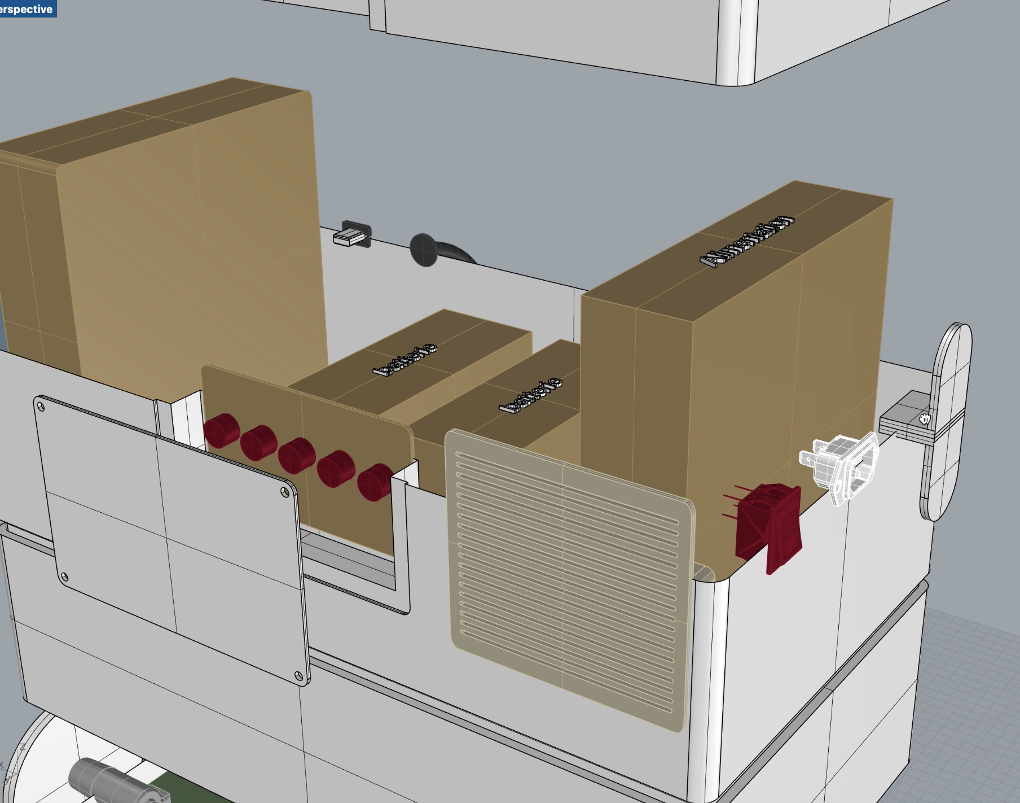
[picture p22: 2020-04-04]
docs/Architecture/pictures/Container (Render 6).png

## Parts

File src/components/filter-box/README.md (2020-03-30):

# Filter Box

| Version | Last Changelog | Ready? | Online CAD Models |
| ------- | -------------- | ------ | ----------------- |
| V0 | Initial design | ❌
| V1 | Hermetic testing, make multiple caps according to needs | ❌ | [link](https://a360.co/33CCX4T)
| V2 | Hermetic testing, make multiple caps according to needs | ❌ | none
| V3 | Add a screwing pitch for lock/unlock | ❌ | none
| V4 | Improved the screwing pitch according to feedback, add markers for easier manipulation | ❌ | none
| V5 | Wall-mountable, 3D-printability optimizations | ❌ | [view model](https://a360.co/2Utff87)

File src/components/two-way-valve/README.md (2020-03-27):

# Two-Way Valve

| Version | Last Changelog | Ready? | Online CAD Models |
| ------- | -------------- | ------ | ----------------- |
| V1 | Initial design | ❌ | [link](https://a360.co/2QNO9q8)

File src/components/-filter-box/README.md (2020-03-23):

# Filter Box

| Version | Team's focus | Ready? | Online CAD Models |
| ------- | ------------ | ------ | ----------------- |
| V0 | Improve design, make multiple caps according to needs | ❌ | [link](https://a360.co/39bRKEN)
| V1 | Hermetic testing, make multiple caps according to needs | ❌ | [link](https://a360.co/33CCX4T)

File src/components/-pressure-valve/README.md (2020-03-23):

# Air Transistor Valve

| Version | Team's focus | Ready? | Online CAD Models |
| ------- | ------------ | ------ | ----------------- |
| V3 | Test flap concept and accuracy | ❌ | none

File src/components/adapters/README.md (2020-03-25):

# Adapters

| Version | Last Changelog | Ready? | Online CAD Models |
| ------- | -------------- | ------ | ----------------- |
| N/A | Add a test lung adapter | ✅ | none

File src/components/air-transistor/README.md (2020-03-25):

# Air Transistor

| Version | Last Changelog | Ready? | Online CAD Models |
| ------- | -------------- | ------ | ----------------- |
| V1 |  | ❌ | [link](https://a360.co/2IS0x3U)
| V2 |  | ❌ | [link](https://a360.co/2Unrwtp)
| V3 | Reduce dead space | ❌ | [link](https://a360.co/3do5uzk)
| V4 | Moved away from the guillotine system | ✅ | [link](https://a360.co/2wy4eZX)

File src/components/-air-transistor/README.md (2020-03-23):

# Air Transistor

| Version | Team's focus | Ready? | Online CAD Models |
| ------- | ------------ | ------ | ----------------- |
| V1 |  | ❌ | [link](https://a360.co/2IS0x3U)
| V2 |  | ❌ | [link](https://a360.co/2Unrwtp)
| V3 | Reduce dead space | ❌ | [link](https://a360.co/3do5uzk)
| V4 (Experimental) | Minimize dead-space, make it simpler to print, simpler to use | ❌ | [link](https://a360.co/2wy4eZX)

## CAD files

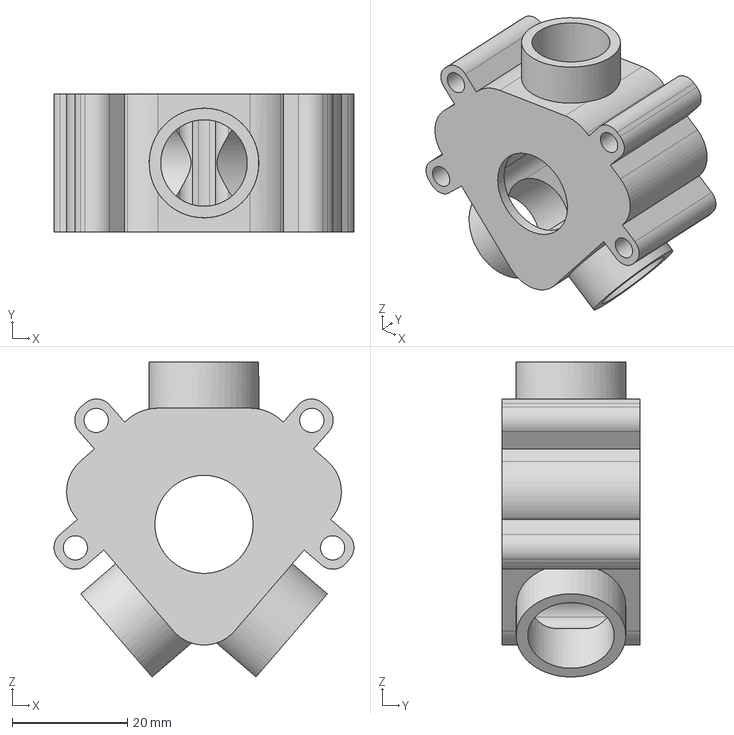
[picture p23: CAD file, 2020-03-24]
src/components/-air-transistor/step/V4/Casing.step
52.0 x 24.0 x 54.6 mm

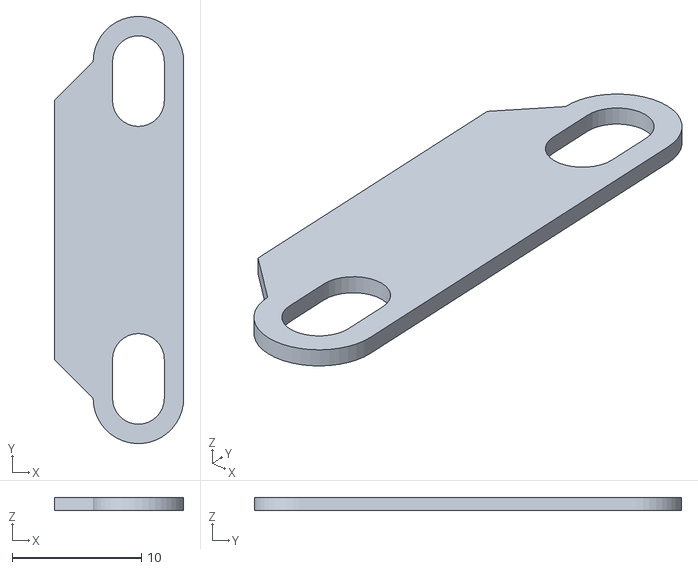
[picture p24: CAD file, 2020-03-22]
src/components/-pressure-valve/stl/Cale_reglage_1mm.stl
10.0 x 33.0 x 1.00

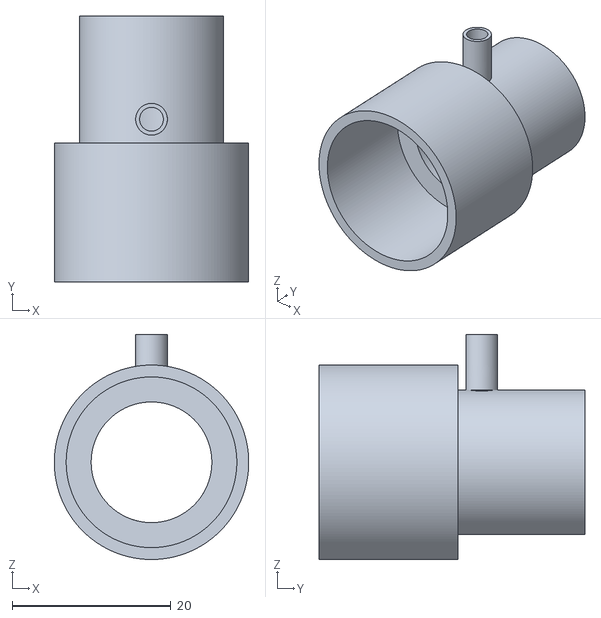
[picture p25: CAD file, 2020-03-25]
src/components/adapters/fdm/stl/Adapter Validation Lung to 15mm.stl
24.5 x 33.5 x 28.3

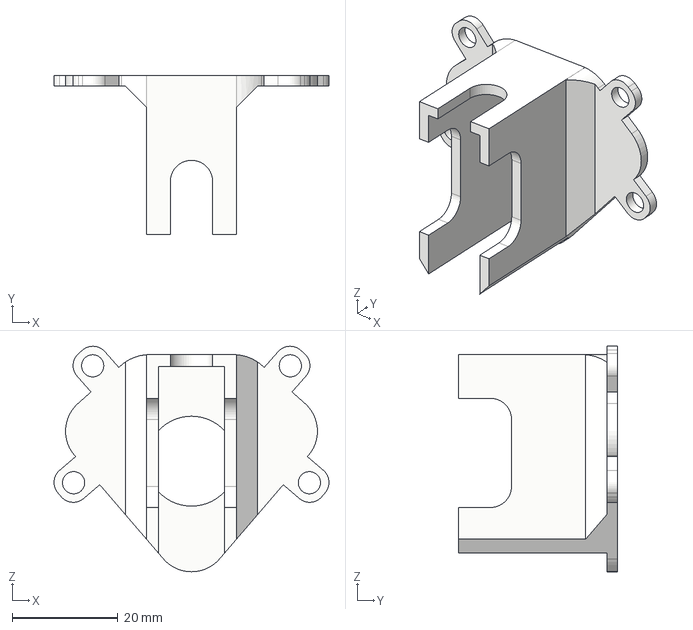
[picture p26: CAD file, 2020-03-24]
src/components/air-transistor/step/V4/Motor Casing.step
52.0 x 30.0 x 42.6 mm

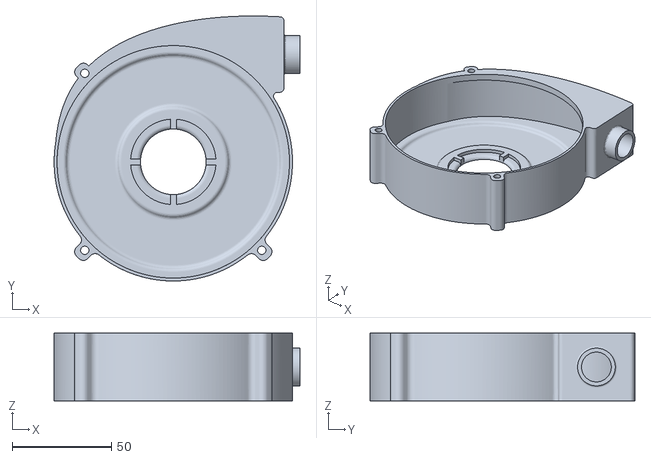
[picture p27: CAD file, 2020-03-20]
src/components/blower/fdm/stl/V7/Blower - Duct.stl
123.7 x 133.4 x 34.0

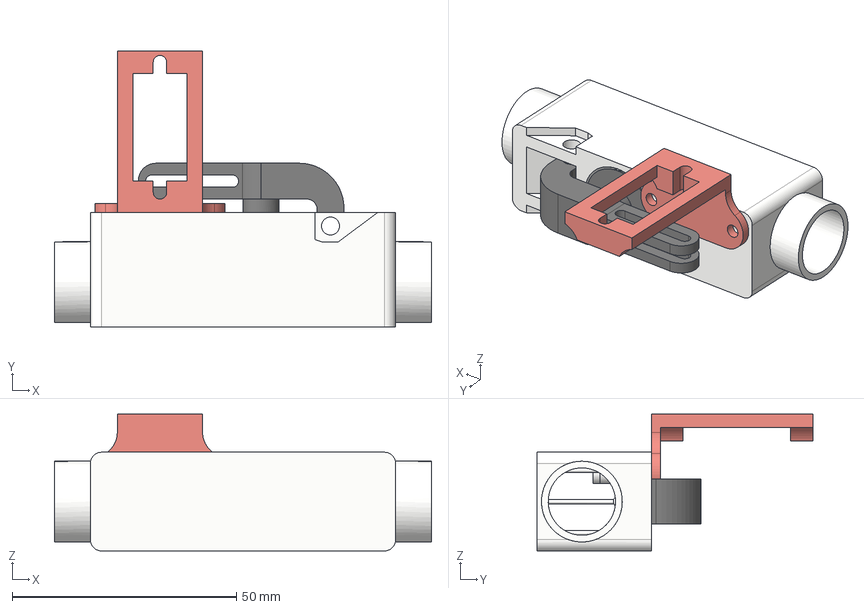
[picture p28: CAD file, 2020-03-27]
src/components/pressure-valve/step/pressure-valve.step
84.0 x 61.5 x 30.5 mm
Core
Shutter
Motor Fit

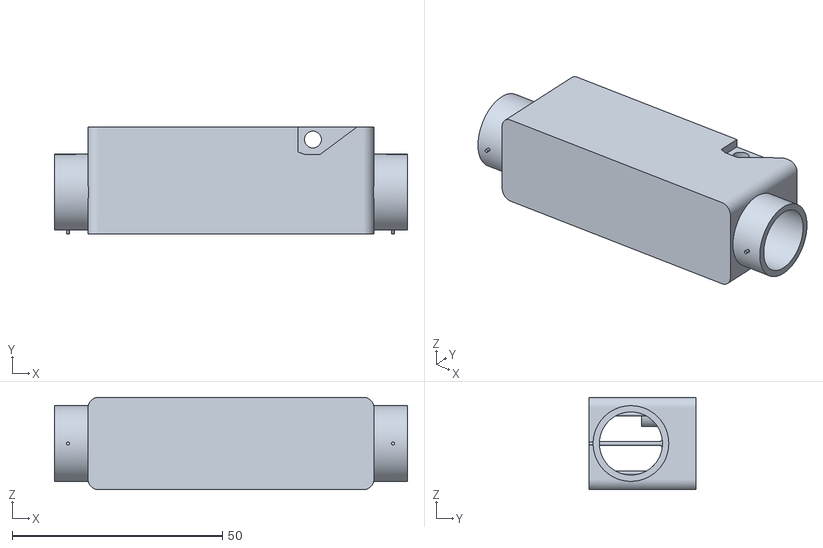
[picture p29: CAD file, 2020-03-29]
src/components/pressure-valve/stl/Core.stl
84.0 x 25.5 x 22.0

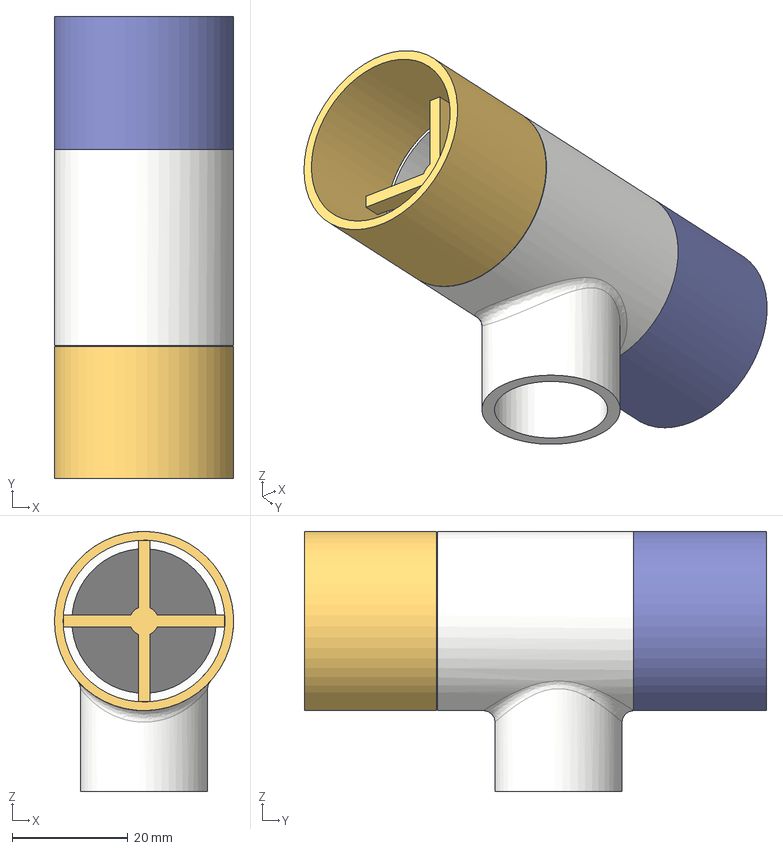
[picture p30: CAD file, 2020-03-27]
src/components/two-way-valve/step/two_way_valve.step
31.0 x 80.0 x 45.0 mm
Valve
One-Way Gate Top
Tube Fit Top
Tube Fit Bottom
One-Way Gate Bottom

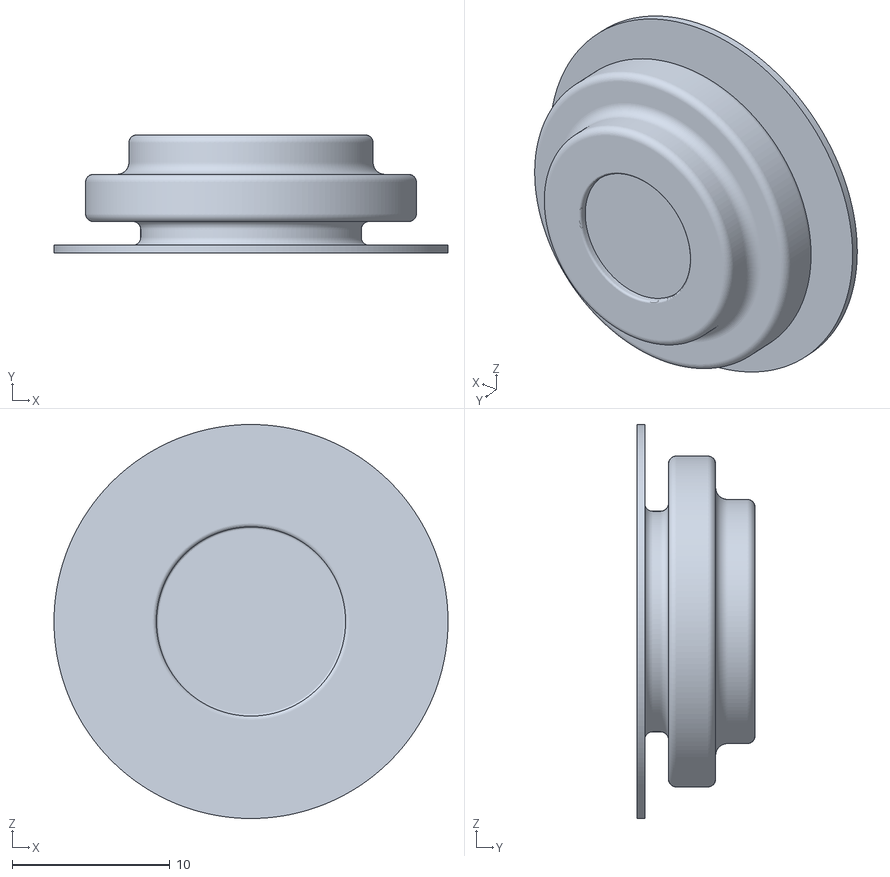
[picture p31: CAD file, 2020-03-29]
src/components/two-way-valve/stl/One-Way Gate Bottom.stl
25.0 x 7.50 x 25.0

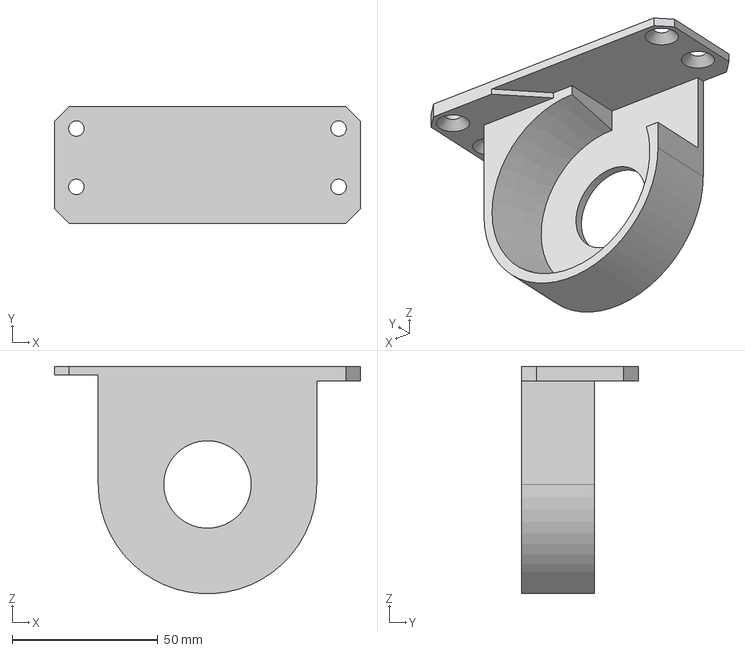
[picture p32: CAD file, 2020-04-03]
src/mechanics/parts/blower-holder/fdm/step/V1/Blower Holder V1 - Core.step
105.0 x 40.0 x 77.9 mm

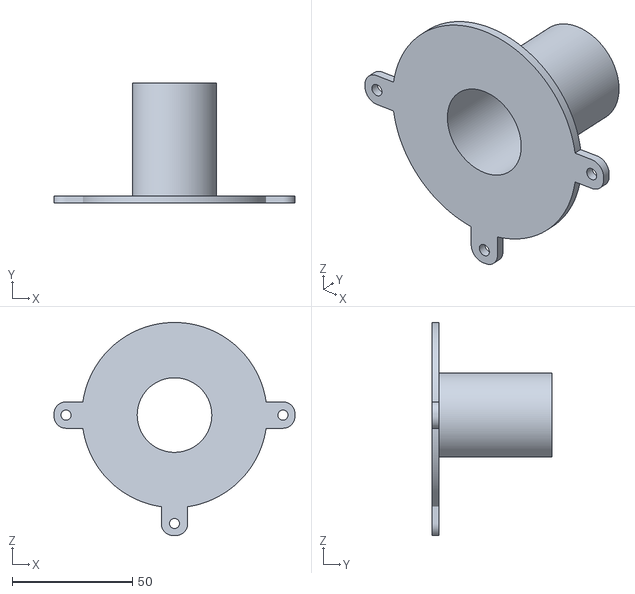
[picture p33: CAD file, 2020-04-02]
src/mechanics/parts/blower-holder/fdm/stl/V1/Blower Holder V1 - Casing/Top.stl
100.2 x 50.0 x 88.6

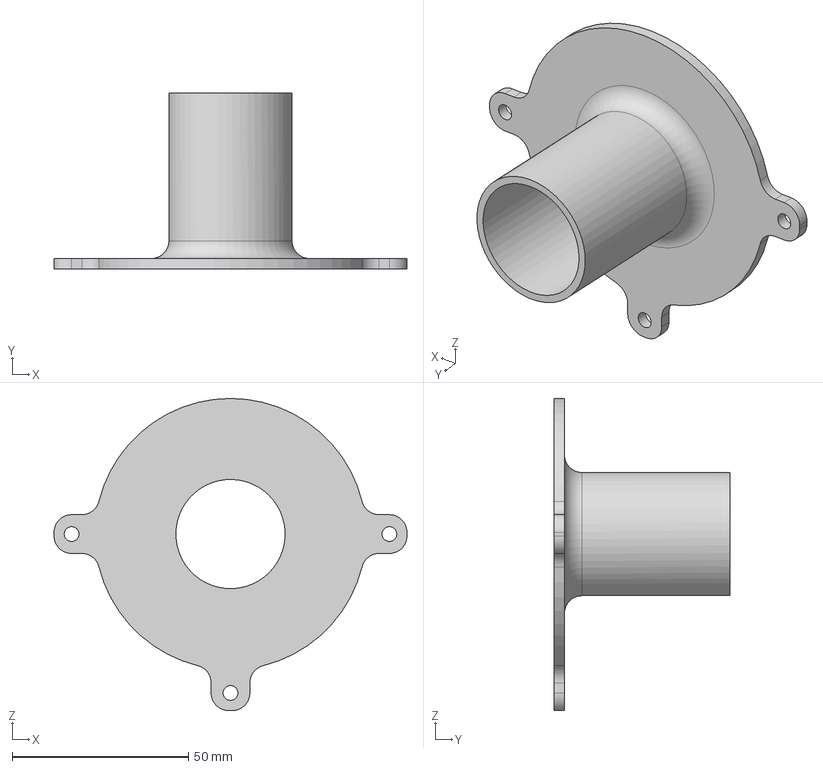
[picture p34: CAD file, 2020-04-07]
src/mechanics/parts/blower-holder/printing/step/V2/Top.step
100.2 x 50.0 x 88.6 mm

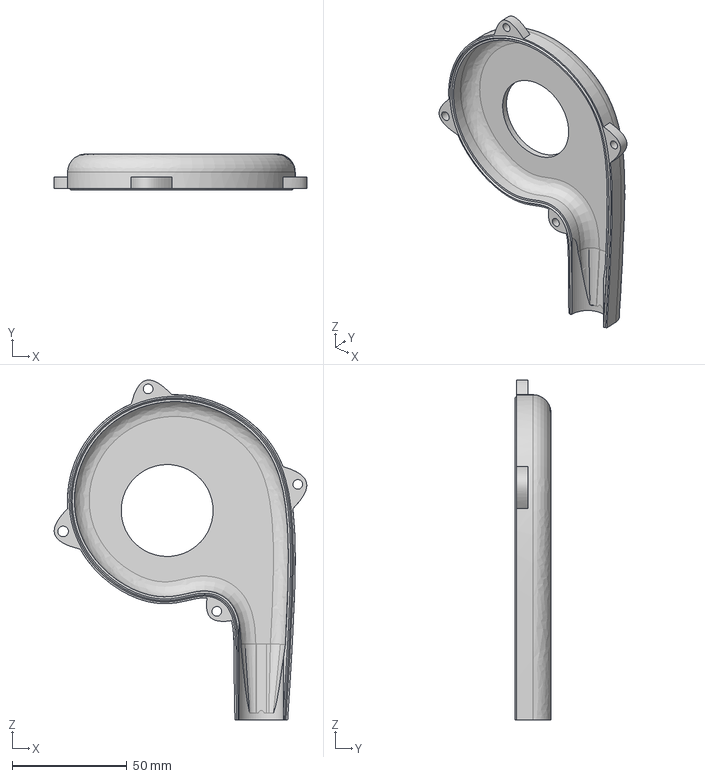
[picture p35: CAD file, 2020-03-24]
src/mechanics/parts/blower/fdm/step/V9/top.step
110.0 x 15.8 x 148.0 mm

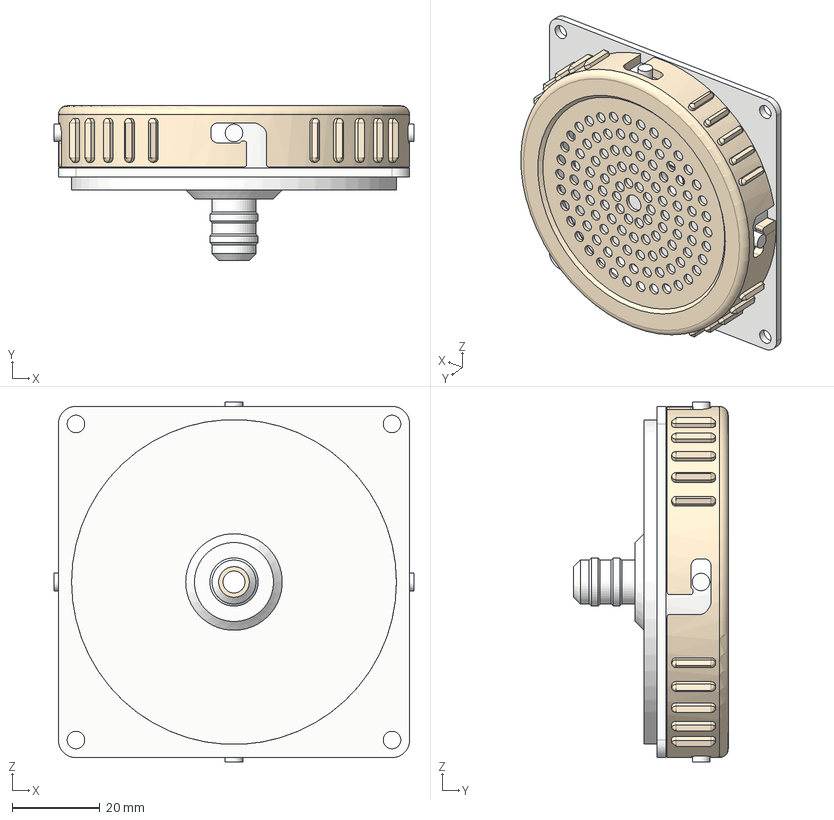
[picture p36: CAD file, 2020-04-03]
src/mechanics/parts/machine-filter-box/fdm/step/V1/Machine Filter Box V1 (Outtake).step
82.0 x 35.2 x 82.0 mm
Basis
Joint
Seal

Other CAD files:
src/mechanics/parts/patient-filter-box/fdm/fusion/Patient Filter Box V4/filter_box_v4.SLDPRT
src/mechanics/parts/pneumatic-connectors/fdm/step/V2/Pneumatic Connectors V1 - Respiratory No Pressure.step
src/components/-air-transistor/cad/Air Transistor V1.f3d
src/components/-air-transistor/cad/Air Transistor V2.f3d
src/components/-air-transistor/cad/Air Transistor V3.f3d
src/components/-air-transistor/cad/Air Transistor V4.f3d
src/components/-air-transistor/step/V3/Box Container.step
src/components/-air-transistor/step/V3/Guillotine Wall.step
src/components/-air-transistor/step/V3/Guillotine.step
src/components/-air-transistor/step/V3/Motor Holder Separator.step
src/components/-air-transistor/step/V3/Roof Hermetic Seal.step
src/components/-air-transistor/step/V3/Roof.step
src/components/-air-transistor/step/V4/Adapter 15-15.step
src/components/-air-transistor/step/V4/Exchanger.step
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

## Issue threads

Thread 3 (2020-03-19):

makers-for-life/makair #3: Choosing the pressure sensor

Benhalor, 2020-03-19:
Hello,

Congratulations on your project. I'm impressed with how fast you're moving!
You said in the video that the pressure would be monitored by a pressure sensor. 

If you need help for choosing the pressure sensor, you can contact me : +33 (0)695358125

Something like this one could be great :
https://fr.farnell.com/honeywell/abpdant005pgaa5/capt-pression-5psi-axial-avec/dp/2490459

0 to 5 PSI sensor, which means 0 to 258,5 mmgh
Absolute Precision : +-1.5%FSS which means +- 0.075 PSI or +-3.9 mmgh
Relative Precision : 0.25%FSS which means +-0.0125 PSI or +-0.64 mmgh
5V sensor, because the arduino uno that you choose is 5V.
through-Hole sensor : easier to solder
14€

Gabriel

waxzce, 2020-03-19:
For the reccord, we did have a call with @Benhalor and solve many problmes thax to him

pi-r-p, 2020-03-20:
Hello, 
I went through the electronic part (respi_V0.fzz) ( @hbs send me a link to the project) , same remarks... In french:

Le capteur MPX10GP n'est pas le meilleur. La plage est bonne (10kPa pour un respirateur, ça va, la pression usuelle montera au grand max à 5kPa ([d'après une doc médicale ici](https://www.srlf.org/wp-content/uploads/2020/03/2020-FP-Respi-3-Principes-ge%CC%81ne%CC%81raux-de-re%CC%81glage-des-modes-contro%CC%82le%CC%81s-et-assiste%CC%81s.pdf)), mais il ne faut pas prendre un modèle avec une sortie différentielle derrière, et encore moins mettre un AOP comme celui là derrière (lm741, ça s'alimente en +/- 15v si vous voulez en tirer qqch, et il faut gérer l'aspect différentiel). 

Nxp fait aussi des modèles plus récents avec électronique intégrée, qui te font une belle sortie rail to rail 0-5V. Typiquement https://www.nxp.com/docs/en/data-sheet/MPX5010.pdf , c'est déjà plus simple à cabler sur un arduino. Prendre un modèle avec tuyaux, dont un reste en l'air à la pression ambiante, typiquement MPX5010DP. L'amplification n'est plus nécessaire, on peut se contenter de baisser la ref anologique de l'ADC (AREF sur un arduino). 

Attention, il faut aussi créer une bonne référence de tension, et isoler la partie capteur/ADC du reste pour pas avoir un signal trop bruité. Sans séparation puissance/controle, le 5V risque de fluctuer à chaque mouvement des servomoteurs, et fausser la mesure de pression. Donc:
- on alimente en 9 ou 12volts
- on met derrière un régulateur 5V à découpage pour l'arduino et les servos (n'importe quel buck 5v trouvé sur le net)
- un régulateur 5v linéaire (un 7805) pour le capteur, avec quelques condos de découplage (470uF derrière le 7805, 100nF au plus proche de l'alim du capteur, soudé dessus de préférence si il n'est pas sur un circuit imprimé). 
- un régulateur 3.3v linéaire sur AREF (3.3v expoiterait mieux la dynamique de l'adc), pareil, avec des condos de découplage.

Et si c'est un capteur Nxp de cette série il faut une procédure de calibration initiale, car c'est pas un capteur super précis. Le capteur Honeywell suggéré par @Benhalor est deux fois plus cher, mais 10 fois plus précis... Mieux vaut prendre celui là !!

À confirmer par un médecin, mais la pression minimale à maintenir en fin d'expiration est importante aussi, d'après le doc dont j'ai mis le lien plus haut.

Pepeuch, 2020-03-21:
Le prix d’un capteur même 10X plus cher est toujours mieux qu’une vie, le problème va être la livraison pour que cela arrive au plus vite, avec les mesures de confinements et donc de livraisons va être un nouveau dileme.

Mefl, 2020-03-24:
@Benhalor a été intégré au slack

closed 2020-03-24 by Mefl

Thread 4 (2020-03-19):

makers-for-life/makair #4: Forms and maps to prepare for contributors willing to help for mass production

Shalf, 2020-03-19:
Why?
Work from a precise cartography of shops/venues, people (and skills), machines, and stocked supplies.

How?
Trough a form, or anything pre-existing that could be remixed and improved.

[This form](https://ventilator.herokuapp.com/) is being shared by the UK gov, and is a good inspiration for what ours could look like.

An AMI (Appel à Manifestation d'Intérêt) is being held by the EU Commission, with French relays, to do a census of companies with 3D printing production capacities willing to help. We took contact.
We are working wth the RFF (Réseau Français des Fablabs) to find a local cartography of this distributed network alredy engaged and willing to help.

valeriansaliou, 2020-03-19:
Excellent, thanks for the information & contact initiative w/ the AMI system.

Shalf, 2020-03-23:
From CS RFFlabs : French makers' data will end up here https://github.com/co-demos/covid-viz/

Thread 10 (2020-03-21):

makers-for-life/makair #10: How does a layman on the subject that has a 3D print can help?

renata-castro, 2020-03-21:
Hello.
today I received the link to this website by a co-worker who is a coder and in our company we have a 3D printer. we would like to help but we want to know if hospitals will accept these parts, if there are no sterilization requirements that would prevent us from providing, in addition to other possible issues. is there an approval from the WHO? what do you recommend before starting the production of the parts? 
thank you.

valeriansaliou, 2020-03-21:
Hello there,

The parts are not yet finalized; we’ll make an announcement whenever the tests were done and that the parts are ready for production.

Regarding the printing material, it has to be as chemically stable as possible, so we’re looking for medical-grade ABS (neutral color), or even PETG.

tuxinoo, 2020-03-21:
PETG is the better choice because it’s a material stronger and safer (ie water bottles and for food) than ABS (toxicity). This project is dealing with patient’s health (safe) and mecanical movements (stronger) so I recommend PETG.
Nylon is also a choice but not all 3D printers are capable to print with.

valeriansaliou, 2020-03-21:
@tuxinoo we have a MakerBot Method at Crisp; a Nylon spool order is on the way, should be received on Monday or Tuesday ;)

tuxinoo, 2020-03-21:
Nylon is a better choice if you have a good 3D printer. ). I have just an Ender 3 at home.

renata-castro, 2020-03-21:
Thank you for the clarification. I've seen an article today that reinforces the need for this:
https://www.3dprintingmedia.network/covid-19-3d-printed-valve-for-reanimation-device/?fbclid=IwAR2gdR9bdaRVP9h7n1xUMNd4cqFSX3PaTXNwH9Y6qe8AMNdxp0OHJ-cnzYE

renata-castro, 2020-03-21:
I'm in contact with a former owner of a hospital in Rio de Janeiro and also trying to get a closer contact to head doctors here in Oregon and California. 
How are you guys planning to distribute and proceed with the sterilization of the pieces?

fr33z00, 2020-03-22:
Silicon is very neutral, as far as I know.
There are two ways of using it: 
- as a cover on any plastic (even PLA, then)
- molded, the mold behing realised in any plastic.

Why-Ty, 2020-03-25:
Bonjour à tous, mon entreprise a une formlab 2 a st Étienne de Montluc et une ultimaker 2 extented+. Nous avons quelques bacs de résine pour la formlab et un peu de PETG (BLEU). Sinon, de l'ABS et pla bien sur. Dites moi si vous avez besoin, je ne suis pas sur place mais je peux voir avec mes collegues. Si vous souhaitez imprimer en PEHD, c'est assez complexe mais j'ai des contact en France qui font ça très bien et j'ai un plateau spécifique pour l'adhérence. A dispo pour toutes infos. Yo

dolmen, 2020-03-31:
See also this project from MIT : https://e-vent.mit.edu/

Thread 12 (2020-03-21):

makers-for-life/makair #12: How can I contribute?

alencarfff, 2020-03-21:
Hello, I'm Felipe, I'm a Brazilian experienced web developer and, I found your project looking for a way to helping against the COVID-19 epidemy. Your project is fantastic and I hope all it works well when finalized. I can help voluntarily to build a website to better promote your project and bring more people to contribute to it. Beyond it, I can help to translate part of the project documentation to PT-BR too.

waxzce, 2020-03-21:
I focus on the prototype delivery, I try to find someone to coordinate with you

alencarfff, 2020-03-22:
Okay. I'll wait for your contact.

HugoGresse, 2020-03-27:
French web dev here
Let us know if you need a build a landing page for MakAir or anything front-related.

eliottvincent, 2020-03-27:
Hello @HugoGresse, I can invite you to our Slack, we have a team already working on the front, I think your help would be appreciated. You can send me a mail at dev at eliottvincent dot com

fareivas, 2020-03-27:
Hello, I am a Braziliam experienced with 3D printing for robotics and firmware development. I am trying to replicate/build your prototipe project here in my city. 
1. Can you provide a bill of materials used so far ?
2. How can I help with my skills?

Best Regards
Fábio

JulienCalvignac, 2020-04-21:
Hello all,

First of all, congratulations for such achievements in such short time!
How can I help  as a volunteer ?

I am a systems engineer/architect with strong background in system architecture (safety), controls, electronics, electricity, embedded software and project management.
I am very familiar with agile and CI development, I can help on such topic as well. I can help also on safety and regulatory compliance.

Let me know !! 
All the best !

Julien Calvignac

NopMicrowave, 2020-04-25:
Hi,

I have seen that you plan to use LoRa Radio scheme (in the telemetry, or wherever you want).
I have more than 10 years of experience in LoRa, LoRaWAN in industrial, city, home, on premise, on Raspberry Pi, on private VPS, ...
If you need some help, you can ask, I will help.

Nop

Nopmicrowave.io

ilyautov, 2020-05-09:
Hello, i'm Russian back-end developer, i have strong experience in node.js, golang and if that reasonable in rust, previously i have some hardware projects and i think  could help
I'm want to help project, may be you have any tasks for me?

BSte77, 2020-05-14:
Hi,
I am from Paris, I can help with 10 years background in robotics systems and custom machines, and 10 years in Li-Ion batteries. 

Wining space in the enclosure by exchanging lead-acid batteries by Li-ion one  could help to win space in order to embed O2 bottle and make the makair portable for medical trips.

Good luck!
Bertrand

eliottvincent, 2020-05-15:
Hello @BSte77 , Li-ion cells is something we would like to work on. I can invite you to our Slack if you provide me your email :)

BSte77, 2020-05-15:
Hi Elliot,
Please find here my email and welcome to your inquiries. Really motivated
to contribute to that project!

I am really new in GitHub with really no knowledge on how to do
collaborative work with this plateform.

Looking forward your return and your advices in order to be the most
efficient as possible 😉

As a first exchange, could you tell me more about :
Voltage, I saw 2 batteries.  Are they connected in series or parallel ?
Maximun Instantaneous power needed
Current avalaible capacity
Environement temperature

As you know, there are some Li-ion batteries avalaible on the market, for
exemple for Ebikes that may ne used.

Bertrand.

BSte77, 2020-05-15:
Hi again Elliot,
I answered directly to your email. Also, did you receive my email address or do I have to share it here ??

eliottvincent, 2020-05-15:
@BSte77 Thanks, you may share it here or send me an e-mail at dev[at]eliottvincent[dot]com if you don't want to display it publicly.

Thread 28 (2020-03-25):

makers-for-life/makair #28: [Soft] be sure that every   pinMode(PIN_SERVO_PATIENT, OUTPUT); is OK

waxzce, 2020-03-25:


jabby, 2020-03-25:
WIP here.
https://github.com/covid-response-projects/covid-respirator/pull/21

dsferruzza, 2020-03-25:
I believe this is already handled by the Servo lib we use? → https://github.com/arduino-libraries/Servo/blob/master/src/avr/Servo.cpp#L241

jabby, 2020-03-25:
I close the issue as it is handled by Servo lib.
Feel free to reopen if needed.

waxzce, 2020-03-25:
but not for every pin, whiuch was my point

dsferruzza, 2020-03-25:
I'm not sure to get your point actually... Both servos are OUTPUT thanks to the lib, right? Do we need more?

jtanguy, 2020-03-26:
Yes, for the buttons, pressure sensor and buzzer. 
There is no pinMode set for any pin in the master branch atm

jabby, 2020-03-26:
Ok I'm on it.

jabby, 2020-03-26:
* Servo: :ok: thanks to the [lib](https://github.com/arduino-libraries/Servo/blob/master/src/avr/Servo.cpp#L241)
* Buttons: :ok: thanks to the lib ([here](https://github.com/rlogiacco/AnalogButtons/blob/master/AnalogButtons.h#L105) and [here](https://github.com/rlogiacco/AnalogButtons/blob/master/AnalogButtons.cpp#L34)) and to our code [here](https://github.com/covid-response-projects/covid-respirator/blob/master/src/arduino/respi_v0.cpp#L188)
* Pressure sensor: missing. `analogRead` does not set the pinMode to `INPUT`.
* Buzzer: not implemented yet.

commit bb049888 (2020-03-26): Merge pull request #33 from covid-response-projects/issue-28

Fix #28 Add missing pinMode
closed 2020-03-26 by Mefl

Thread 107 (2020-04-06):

makers-for-life/makair #107: Software: implement alarms

csommelet, 2020-04-06:
Alarms logic is currently missing.

Related issues describing alarms individually (alarms definition is still work in progress):
 - RCM-SW-19 - Low plateau pressure - https://github.com/covid-response-projects/covid-respirator/issues/99
 - RCM-SW-18 - High plateau pressure - https://github.com/covid-response-projects/covid-respirator/issues/98
 - RCM-SW-14 - Plateau not reached - https://github.com/covid-response-projects/covid-respirator/issues/64
 - RCM-SW-15 - PEEP not reached at 3rd cycle - https://github.com/covid-response-projects/covid-respirator/issues/65
 - RCM-SW-3 - PEEP not reached at 4th cycle - https://github.com/covid-response-projects/covid-respirator/issues/53
 - RCM-SW-8 - Pressure out of range - https://github.com/covid-response-projects/covid-respirator/issues/58
 - RCM-SW-2 - Low Pressure - https://github.com/covid-response-projects/covid-respirator/issues/52
 - RCM-SW-1 - High Pressure - https://github.com/covid-response-projects/covid-respirator/issues/51
 - RCM-SW-16 - Mains disconnected - https://github.com/covid-response-projects/covid-respirator/issues/70
 - RCM-SW-11 - Low battery - https://github.com/covid-response-projects/covid-respirator/issues/63
 - RCM-SW-12 - Very Low battery - https://github.com/covid-response-projects/covid-respirator/issues/59

Alarming system behavior:
- RCM-SW-13 - Maintain PEEP during high prio alarm - https://github.com/covid-response-projects/covid-respirator/issues/62
- RCM-SW-10 - 'Silence Alarm' button should reset 2min timer - https://github.com/covid-response-projects/covid-respirator/issues/61
- RCM-SW-9 - New alarm should cancel Mute - https://github.com/covid-response-projects/covid-respirator/issues/60

Test benches protocols:
https://docs.google.com/document/d/1A3L-puGiDQOrkns229-GeCmOXisWVPol59NXHKI1Foo/edit

dsferruzza, 2020-04-06:
_I'll try to sum up my understanding._

Alarms have:

- **a trigger predicate:** it can depend on various parameters, and may need an internal counter of the number of cycles in a row the predicate was true along with a threshold that will raise an alarm when exceeded
- **an error code** (unique)
- **a severity:** low, medium, high

When an alarm is triggered it has effects depending on its severity:

- buzzer (already implemented)
- LEDs
- display error codes on the third line of the LCD screen (using horizontal auto-scrolling?)

When several alarms are triggered at the same time, only the alarms of the higher triggered severity have effects.

If a user press the _alarm OFF_ button, it snoozes the buzzer for 2 minutes. If an alarm of higher severity is then triggered, snoozing is interrupted and buzzer rings.

If an alarm's predicate becomes false, it is not to be considered active anymore. Effects can continue to happen according to the higher severity of the remaining active alarms, or stop if there are no remaining active alarms.

---

I believe we need some kind of alarm controller (singleton?) that could:

- be called if the predicate of an alarm is true (this might trigger effects)
- be called if the predicate of an alarm is false (this might stop effects)

It would then keep track and handle:

- inner state of alarms (number of cycles in a row it was triggered)
- active alarms
- snooze status (if snoozed, we need to keep track of the timing and the severity that was snoozed)
- LEDs effects
- LCD display

RomainBlanc, 2020-04-07:
When an alarm is triggered, the alarms number will be displayed on the third line of the screen:

[image]

RomainBlanc, 2020-04-07:
[image]
French version

Mefl, 2020-04-07:
due to #120, we need to store the cycle number for each alarm triggered to be able to send the new alarms (ie triggered in the last complete cycle)

hbs, 2020-04-14:
Alarms should trigger telemetry events, so should the user actions.

closed 2020-05-16 by dsferruzza

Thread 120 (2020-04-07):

makers-for-life/makair #120: telemetry protocol

Mefl, 2020-04-07:
The V1 card is connected to a second device (maybe a raspberry pi) to grab the data and publish the telemetry to the graphical screen or to a central control point via LoRa.

This issue document the exchanges from the F411RE card and the collector (the raspberry pi).

It can send 3 types of information row :

- the data snapshot, sent at each tick, so every 1/100s.
- the machine state snapshot, sent at the beginning of every respiration cycle, so about 35 times per minutes
- the alert trap, sent each time an alarm is triggered and each time the alarm disappear.

Each of theses informations schemes are defined in a proper comment.

Mefl, 2020-04-07:
The data snapshot (sent each 1/100s)

Data is composed with 9 fields, each field is written in binary to compress the data flow (as these exchange will not be used to be human readable).

- The MCU serial ID, to identify the machine (96bits)
it can be retrieved at `*(uint32_t*)(UID_BASE)` : 
`Serial.println("UID [HEX] : "+String(*(uint32_t*)(UID_BASE), HEX)+" "+String(*(uint32_t*)(UID_BASE+0x04), HEX)+" "+String(*(uint32_t*)(UID_BASE+0x08), HEX));`

- the Systick of the STM32 (64bits)
- centile number (16bits)
- current pressure (16bits)
- phase and sub-phase number encoded as it :
* Inspiration - inspi = 17
* Inspiration - hold = 18
* Expiration - expi = 68
* Expiration - hold = 72
So the phase is coded on the 4 high bits, and the subphase is coded on least 4 bits

- blower valve position (8 bits)
- patient valva position (8 bits)
- blower rpm (8 bits)

- battery level (8 bits)

all theses fields are separed by <tab> char.

Mefl, 2020-04-07:
alarm Trap 

- The MCU serial ID, to identify the machine (96bits)

- the Systick of the STM32 (64bits)

- centile number (16bits)

- current pressure (16bits)

- phase and sub-phase number

- the cycle number (32 bits)

- the alarm code
- the alarm level 

- triggered / untriggered toggle encoded as it :

> if triggered => the 4 high bits are HIGH and the 4 least are LOW (11110000)
> if suppression msg => the 4 high bits are LOW and the 4 least are HIGH (00001111)

- wanted value
- measured value 

- duration of the alarm in cycle count (0 for trigger message)

fpistm, 2020-04-08:
> * The MCU serial ID, to identify the machine (96bits)
>   it can be retrieved at `*(uint32_t*)(UID_BASE)` :
>   `Serial.println("UID [HEX] : "+String(*(uint32_t*)(UID_BASE), HEX)+" "+String(*(uint32_t*)(UID_BASE+0x04), HEX)+" "+String(*(uint32_t*)(UID_BASE+0x08), HEX));`

FYI, one other way could be to use LL:
```
#include "stm32yyxx_ll_utils.h"
...
  Serial.printf("%x%x%x\n", LL_GetUID_Word0(), LL_GetUID_Word1(), LL_GetUID_Word2());
```

Mefl, 2020-04-08:
all the pressure values are in mmH2O, so the typical plateau is around 300, and the peep around 80

ThomasL01, 2020-04-10:
Hello, I have started a PR for this topic #141
Feel free to comment and propose solution and idea.

pi-r-p, 2020-04-11:
A quick look at UART performance, with HardwareSerial lib : 
- There is no DMA implemented
- There is no hardware FIFO (because the CPU is DMA capable...)
- There is a 64 bytes software FIFO. It means an interrupt is triggered after each byte confirmed sent to push the next byte into TX register.

At 115200 baud:
- Transmission of 1 to 62 bytes take 50µs CPU time when calling Serial6.print (constant time)
- If you want to send X bytes with X greater than 62 bytes, calling Serial6.print takes 50µs+(X-62)*95µs (mean, see measures)

Measures at 115200 bauds:

| byte count | blocking time | time on tx line |
|--|--|--|
| 1 | 50 µs | |
| 62 | 50µs | |
| 128 | 6.1ms | 12.1 ms |
| 256 | 18.2ms | 24.2ms |

Effective max bandwith with the interrupt overhead is  10.5 ko/s (without any other preemptive interrupts)

fpistm, 2020-04-12:
Buffer size can be increased:
https://github.com/stm32duino/Arduino_Core_STM32/blob/61b14ecb4ce640bbb37b733791b51aa28d906e56/cores/arduino/HardwareSerial.h#L43-L48

IRQ prio is 1 so not advised to increase to 0 as 0 is used for the systick : 
https://github.com/stm32duino/Arduino_Core_STM32/blob/61b14ecb4ce640bbb37b733791b51aa28d906e56/cores/arduino/stm32/uart.h#L53

pi-r-p, 2020-04-12:
Not easily... I tried  `#define SERIAL_TX_BUFFER_SIZE 200` before including anything else, but no way to compile in the order I want.

fpistm, 2020-04-12:
Use this:
https://github.com/stm32duino/wiki/wiki/Customize-build-options-using-build_opt.h

dsferruzza, 2020-04-12:
@fpistm How does it work with Arduino CLI?

It seems I already have `build.xSerial=-DHAL_UART_MODULE_ENABLED` in my `Arduino15/packages/STM32/hardware/stm32/1.8.0/platform.txt` file. If I want to add another option like `-DSERIAL_RX_BUFFER_SIZE`, where should I put it?

fpistm, 2020-04-12:
Add a file named `build_opt.h` in your 'sketch' folder, which is (if I'm not wrong) : `src/software/firmware/srcs`

Then in this file add `-DSERIAL_TX_BUFFER_SIZE 256`
Note that I used a  "power of 2" buffer size which is recommended for ease modulo operation.

fpistm, 2020-04-12:
I've tested and redefinition works as expected.
I've made a mistake in my previous post to the content, I've forgot an '=', I've edited my comment.

pi-r-p, 2020-04-12:
Tested, it works. Nice. 
That's kind of weird to have a header file in the srcs directory... But it is working. Don't forget to `rm -rf /tmp/arduino-*` before compiling again.

fpistm, 2020-04-12:
I know .h is not a good extension but Arduino IDE could only  create file with .h, .hpp, .c, .cpp and .ino extension. That's why .h is used.
For the clean you could use arduino-cli cache clean before the first build with a build_opt.h file

valeriansaliou, 2020-04-14:
As a note discussed w/ @dsferruzza this morning: we should go for a pure-binary protocol, where the receiver parses the packets by simple binary array dereferencing. The first 8 bits should contain the protocol version (eg. V1 as 00000000, V2 as 00000001, etc.). This way the receiver can handle version changes smoothly and support multiple firmware / board versions.

nimamoslemy, 2020-05-03:
Hi, we are a team that needs your feedback to complete our idea.
Please visit our pages and comment on it. 
[github](https://github.com/nimamoslemy/ventilator)
[gitlab](https://gitlab.com/nimamoslemy/avp-ventilator)

closed 2020-05-16 by dsferruzza

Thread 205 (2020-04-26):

makers-for-life/makair #205: Use of pneumatic air line to replace the blower.

bruprescott, 2020-04-26:
Is it possible to use a pneumatic air line instead of the blower?

Here in Brazil, all campaign beds are equipped with hospital pneumatic air and oxygen lines.
Could you add a pressure sensor to guarantee the maximum input value?

valeriansaliou, 2020-04-29:
Hello!

We already have a pressure sensor in the system, which helps perform a PID to adjust the blower speed (through the pinch valves) in order to reach the target pressure.

That means that blower speed is static in practice, and that airflow pressure is managed solely through the pinch / pressure valves. Thus, removing the blower and connecting directly on an external pressure system could work for you, in theory.

bruprescott, 2020-04-29:
Hello Valeriansaliou,
I analyzes the code and wanted to confirm if it was possible, I will try to reproduce it here and return with the analysis.  I‘m a volunteer here in Brazil to contribute to the fight against the covid-19.  Our health care system is collapsing and I‘m willing to use all the resources of my own company to help save lives.  
Doubts: Your datasheet does not contain the values   of the integrated circuits, but from the photos I noticed that they used drivers for the pressure valve servos.  It is not clear how the hardware will be managed.  I saw your v7 valve that uses a brushed motor with planetary reduction and encoder.  But in the code I did not identify the input for managing the encoder.  Regarding the sensor, which model do you use differential pressure sensor?  (MPX5xxx) or Honeywell?  I saw that it also includes input for flow sensor but it is not soldered on the board, will it be implemented in the future to measure the flow?  Could you help me, so that I can replicate some of the hardware for testing?

valeriansaliou, 2020-04-30:
@pi-r-p ; can you help on this? Not sure I can answer on those specific questions.

pi-r-p, 2020-04-30:
Hello, 
We play with the blower speed to avoid a huge max pressure, and the pinch valve may not support the 4bars of a pneumatic outlet. You will need something to get 70cmH2O from the mural outlet if you don't want to blow lungs up.

Indeed, we masked the sensor references in the schematic because the sensor market is really complicated right now. Everyone wants pressure sensor. You can take anything that can measure up to 80cmH2O. 
In the v7, we use a brushless motor with a reduction. There is a lot of electronics included in the motor itself that allow auto homing (find the zero index with an external optical sensor), then you can directly send a PWM as an angle. Nice piece of tech, but also hard to find on the market. I am currently working on a steppers motors version, easier to source.

bruprescott, 2020-05-01:
My idea is to use an inlet pressure regulator, a solenoid to stop the compressed air and a safety relief valve. A pressure sensor must monitor the input line to ensure that everything is within the parameters.

Regarding the pressure sensors, I have enough quantity to meet these specifications.
I don't have a flow sensor, mouser.com has a stock price around 120 USD.

I know these engines, I've used similar ones in robotic submarine projects.
Stepper motors are easy to purchase, low cost, good torque and easy to implement. The best substitute for this application.

About the hardware: could you provide me with an ics reference?
U1, U5, U11, U17, U18, U19, STM NUCLEO (32F303 or 2F411?)

About the firmware:
Is the weaning function expected for subsequent updates?
SIMV, SBT?

bruprescott, 2020-05-02:
@valeriansaliou 

Can these questions be answered publicly or only after the project is fully consolidated?

nimamoslemy, 2020-05-03:
Hi, we are a team that needs your feedback to complete our idea.
Please visit our pages and comment on it. 
[github](https://github.com/nimamoslemy/ventilator)
[gitlab](https://gitlab.com/nimamoslemy/avp-ventilator)

bruprescott, 2020-05-04:
Hello,

I managed to assemble the entire circuit, with step down converters, and more channels for pressure sensors.
I found SMI sensors with higher precision than MPX, with a close cost. It uses i2C 16bit resolution.

My idea is to use a Venturi tube and differential pressure sensor to measure the inspiration and expiration flow.

Could you help me with the implementation of PRVC, ACV controls?

valeriansaliou, 2020-05-04:
@pi-r-p :)

pi-r-p, 2020-05-04:
Hi, 
Problem with the mass flow meter is global sensor availability. We tried venturi tube, mass flow meters, and we still struggle on differential pressure sensor availability. Sensirion is a good example of overstressed company right now. You have to place an order with 40% prepayment without any delivery delay, then wait for their feedback to have a delay... within 12 weeks.
If I look at SMI SM9233 sensor (perfect for a venturi), there is nothing available on the market.

PRVC is not yet implemented, we currently work with pressure only. Volume is a great indication for obstructive cases, so we need to add it, and we are working on it.

bruprescott, 2020-05-05:
Hi @pi-r-p 

I got the following models of differential sensor in stock:
SM9333
SM9541
SM7321

The model SM9233 (Gauge Pressure Digital Sensor, 0 to +250 Pa) has 98 units in stock.

Hi @p,

I got the following models of differential sensor in stock:
SM9333
SM9541
SM7321

The model SM9233 (Gauge Pressure Digital Sensor, 0 to +250 Pa) has 98 units in stock.

I added two drivers for stepper motors, and input for optical sensors.

closed 2020-05-06 by bruprescott

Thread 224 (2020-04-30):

makers-for-life/makair #224: Control: Graph rendering issues

BlackYoup, 2020-04-30:
So I've be digging a bit into the graph rendering problems. There are mostly 3 issues:

- We render more pixels than the chart's drawing area has. Currently the chart drawing area is ~730px large but we store ~900 points (100 points per second * 9). Which makes 1.2 points per pixel. This might be an issue (see https://github.com/38/plotters/issues/136#issuecomment-621292991). You can get the drawing area using https://docs.rs/plotters/0.2.12/plotters/chart/struct.ChartContext.html#method.plotting_area

- We receive the pressure through the Telemetry in the `mmH2O` unit and we then render the graph using the `cmH20` unit. We currently divide the pressure using a simple `/ 10` which is wrong because it drops the decimal values and make the graph renders approximate values, creating a "stairs" effect. We could instead try to render by keeping the decimals. I tried that and it makes the graph render a bit better and smoother but another problem arises: because the values move a lot (127, 128, 129, 128, ...), the rendered line won't be "flat" even though the values are very close. Instead, we will be able to see multiple dots, one for each value. I only tried with a stroke_width of 1, maybe it's better with a stroke_width of 2 but I don't think so.

- The pressure values received from the telemetry may vary. Some values go a bit too high (or too low) compared to the graph's "trajectory". The issue is way more visible with a stroke_width of 2 than it is with a stroke_width of 1. This causes some sort of "spikes" rendered.

For example, here are some values received from the telemetry, extracted from the "long" recording:
```
2020-04-29T23:50:43.500160221Z: 238,
2020-04-29T23:50:43.490150221Z: 247,
2020-04-29T23:50:43.480140221Z: 238,
2020-04-29T23:50:43.470129221Z: 241,
2020-04-29T23:50:43.460119221Z: 238,
```

The variation is quite huge and it becomes way harder to draw a smooth graph line with those. I'm pretty sure that's normal behaviour but should we try to sleek them?

cc @valeriansaliou @dsferruzza

valeriansaliou, 2020-04-30:
Thanks for the details; I've tried doing a quick native display in mmH20 and the graph indeed looked much smoother. I have a ToDo to implement a permanent, clean fix for that on next Friday.

baptistejamin, 2020-05-02:
Your master solved the problem using a low pass filter.

closed 2020-05-02 by baptistejamin

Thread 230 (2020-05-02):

makers-for-life/makair #230: Question about UI design

FabriceSalvaire, 2020-05-02:
I just looked the "very unusual and complicated" (*) code of the control UI. ( * in comparison to many UI frameworks used in the industry )

I wonder why you didn't use the framework https://www.qt.io/qt-in-medical instead. For example, this medical device https://www.medec-intl.com/products/anaesthesia/caelus/ uses Qt for its touch user interface.  It is a good point that a framework like Qt has embeded industrial implementations.

Rust is an interesting new language, like many other experimental languages but for the UI of a medical device ???

Moreover the fact the UI system requires a X11 server on a Raspberry Debian looks funny for a true medical device.  Qt can run on many platforms and in particular on bare metal.

waxzce, 2020-05-02:
Hi

We choose the raspi essentially for a stock availability perspective, and since the UI part is not on the critical path but essentially listening logs, it can be a Linux without very big problems, even if it's suboptimal. 

The choice of rust is more for the security and resiliency it allows to use, but as you can see, the project is modular, so another UI can be written, and in the future we can remove the raspi for something smaller if we find some availability.

So, feel free to create another UI, but I will not go for the eternal language/framework debate here ;-).
In software like in every part of the project, we do favorite multiple solutions and parallel experimentations.

waxzce, 2020-05-02:
I close the issue, reopen if you need a repo for your QT UI

closed 2020-05-02 by waxzce

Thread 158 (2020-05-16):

### ISSUE TITLE
State management - reset & initialize

### ISSUE THREAD

**Issue by eliottvincent** [makers-for-life/makair#158]
Implementing the state management of the whole system (i.e. blower, valves, alarms, etc.) could be great.
Methods:
- reset --> clear the state and all its variables
- initialize --> set variables to their default values

This would allow us to start from a clean state and avoid being in a weird state.
Please close if this is already implemented.

**Comment by dsferruzza** [comment]
I believe this is already done, but maybe we should discuss this in more details to make sure our visions are aligned

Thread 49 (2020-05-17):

### ISSUE TITLE
Ventilation Specifications

### ISSUE THREAD

**Issue by simonsan** [makers-for-life/makair#49]
Some information on `Ventilation Specifications`:

From the Clinical Guidance this document summarizes the minimum set of requirements for ventilation:
https://e-vent.mit.edu/clinical/key-ventilation-specifications/

Also some more engineering specifications from the University of Florida:
https://simulation.health.ufl.edu/technology-development/open-source-ventilator-project/

One thing to keep in mind as well, that could be solved in the early design stages:

"The American Society of Anesthesiologists issued [guidance](https://www.asahq.org/about-asa/governance-and-committees/asa-committees/committee-on-occupational-health/coronavirus) on Feb. 23 discouraging CPAP use in COVID-19 patients — advice largely informed by experience with the SARS epidemic in 2003. Studies dating to 2003 suggest that such devices can pump viruses into the air, potentially increasing the spread of a contagious disease.

During the SARS outbreak in Toronto, half of all SARS cases, including three deaths, occurred among health care workers. Some of the greatest risk arose when doctors and nurses were exposed to aerosolized virus through the use of positive airway pressure machines or other respiratory therapy devices." ([Source](https://www.npr.org/sections/health-shots/2020/03/27/822211604/cpap-machines-were-seen-as-ventilator-alternatives-but-could-spread-covid-19?t=1585487737279))

**Comment by eliottvincent** [comment]
Thanks a lot for the documentation, and the concerns about virus rejection in the room's air. We already have measures in place to lower the risk of aerosolized virus (multiple filters).

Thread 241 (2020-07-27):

makers-for-life/makair #241: Blower motor details

ilyautov, 2020-07-27:
Hi!.
We started research and development for build engine for blower. We found engineer who can made that.
We decided to pay in full for this work and transfer that to the Makair project as our contribution to the common cause.
For design this we need the parameters of the engine. We need the maximum and minimum engine rotatios per minute, as well as their dependence on the control signal from the board (the so-called timing diagram).
https://blog.avislab.com/uploads/2013/05/brushless3_4.png

ilyautov, 2020-07-27:
@pi-r-p @valeriansaliou can you help us?

pi-r-p, 2020-07-27:
Hi, you plan to build a brushless motor on your own ?
The main blower challenge is not really the motor, but the blower itself, with a perfect balance to spin at full speed without too much vibration.
The challenge is the motor+rotor and turbine.

Globally, the blower must achieve this:
[image]

or this (red curve for 24V)
[image]

Current blower is around 40000rpm
If you can achieve this with less than 40000rpm, that could be great too.

Next issue is the noise... It is highly linked to the blower design. What we saw in medical blowers we teared down is that it is common to sacrifice efficiency to avoid high frequency noise.

Timing diagram is not that much important compared to other blower challenges. We also used sensorless ESC that did a really good job (drone ESC).

ilyautov, 2020-07-29:
Hi, @pi-r-p thank you for your response that is will be helpful for build.
Yes, i think we can try to design full set of motor, rotor and turbine.
Can we chat about that directly? for example in telegram or email: @wh_zt ilyautov@gmail.com
Can you advice to us any motor which we can use with blower v14 for start redesign?  F.e: Parrot Bebop Drone 2 Motor Kit or Parrot Anafi motor kit?

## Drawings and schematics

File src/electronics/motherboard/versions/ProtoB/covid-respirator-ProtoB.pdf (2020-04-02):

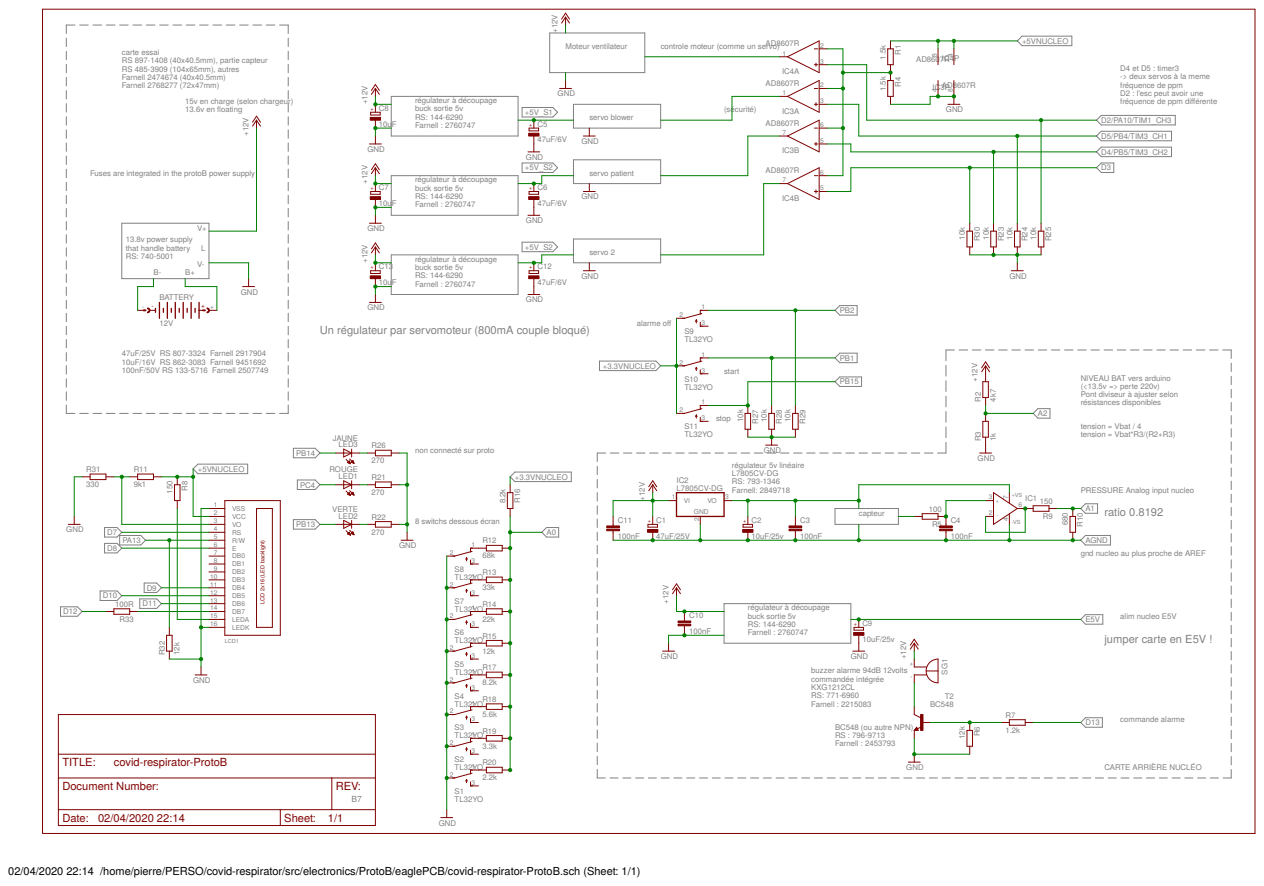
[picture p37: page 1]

carte essai
RS 897-1408 (40x40.5mm), partie capteur RS 485-3909 (104x65mm), autres Farnell 2474674 (40x40.5mm)

15v en charge (selon chargeur)
13.6v en floating

Fuses are integrated in the protoB power supply

Un régulateur par servomoteur (800mA couple bloqué)

NIVEAU BAT vers arduino
(<13.5v => perte 220v)
Pont diviseur à ajuster selon
résistances disponibles

non connecté sur proto

AGND
gnd nucleo au plus proche de AREF

Document Number: | REV: B7

Date: 02/04/2020 22:14 | Sheet: 1/1

02/04/2020 22:14 /home/pierre/PERSO/covid-respirator/src/electronics/ProtoB/eaglePCB/covid-respirator-ProtoB.sch (Sheet: 1/1)

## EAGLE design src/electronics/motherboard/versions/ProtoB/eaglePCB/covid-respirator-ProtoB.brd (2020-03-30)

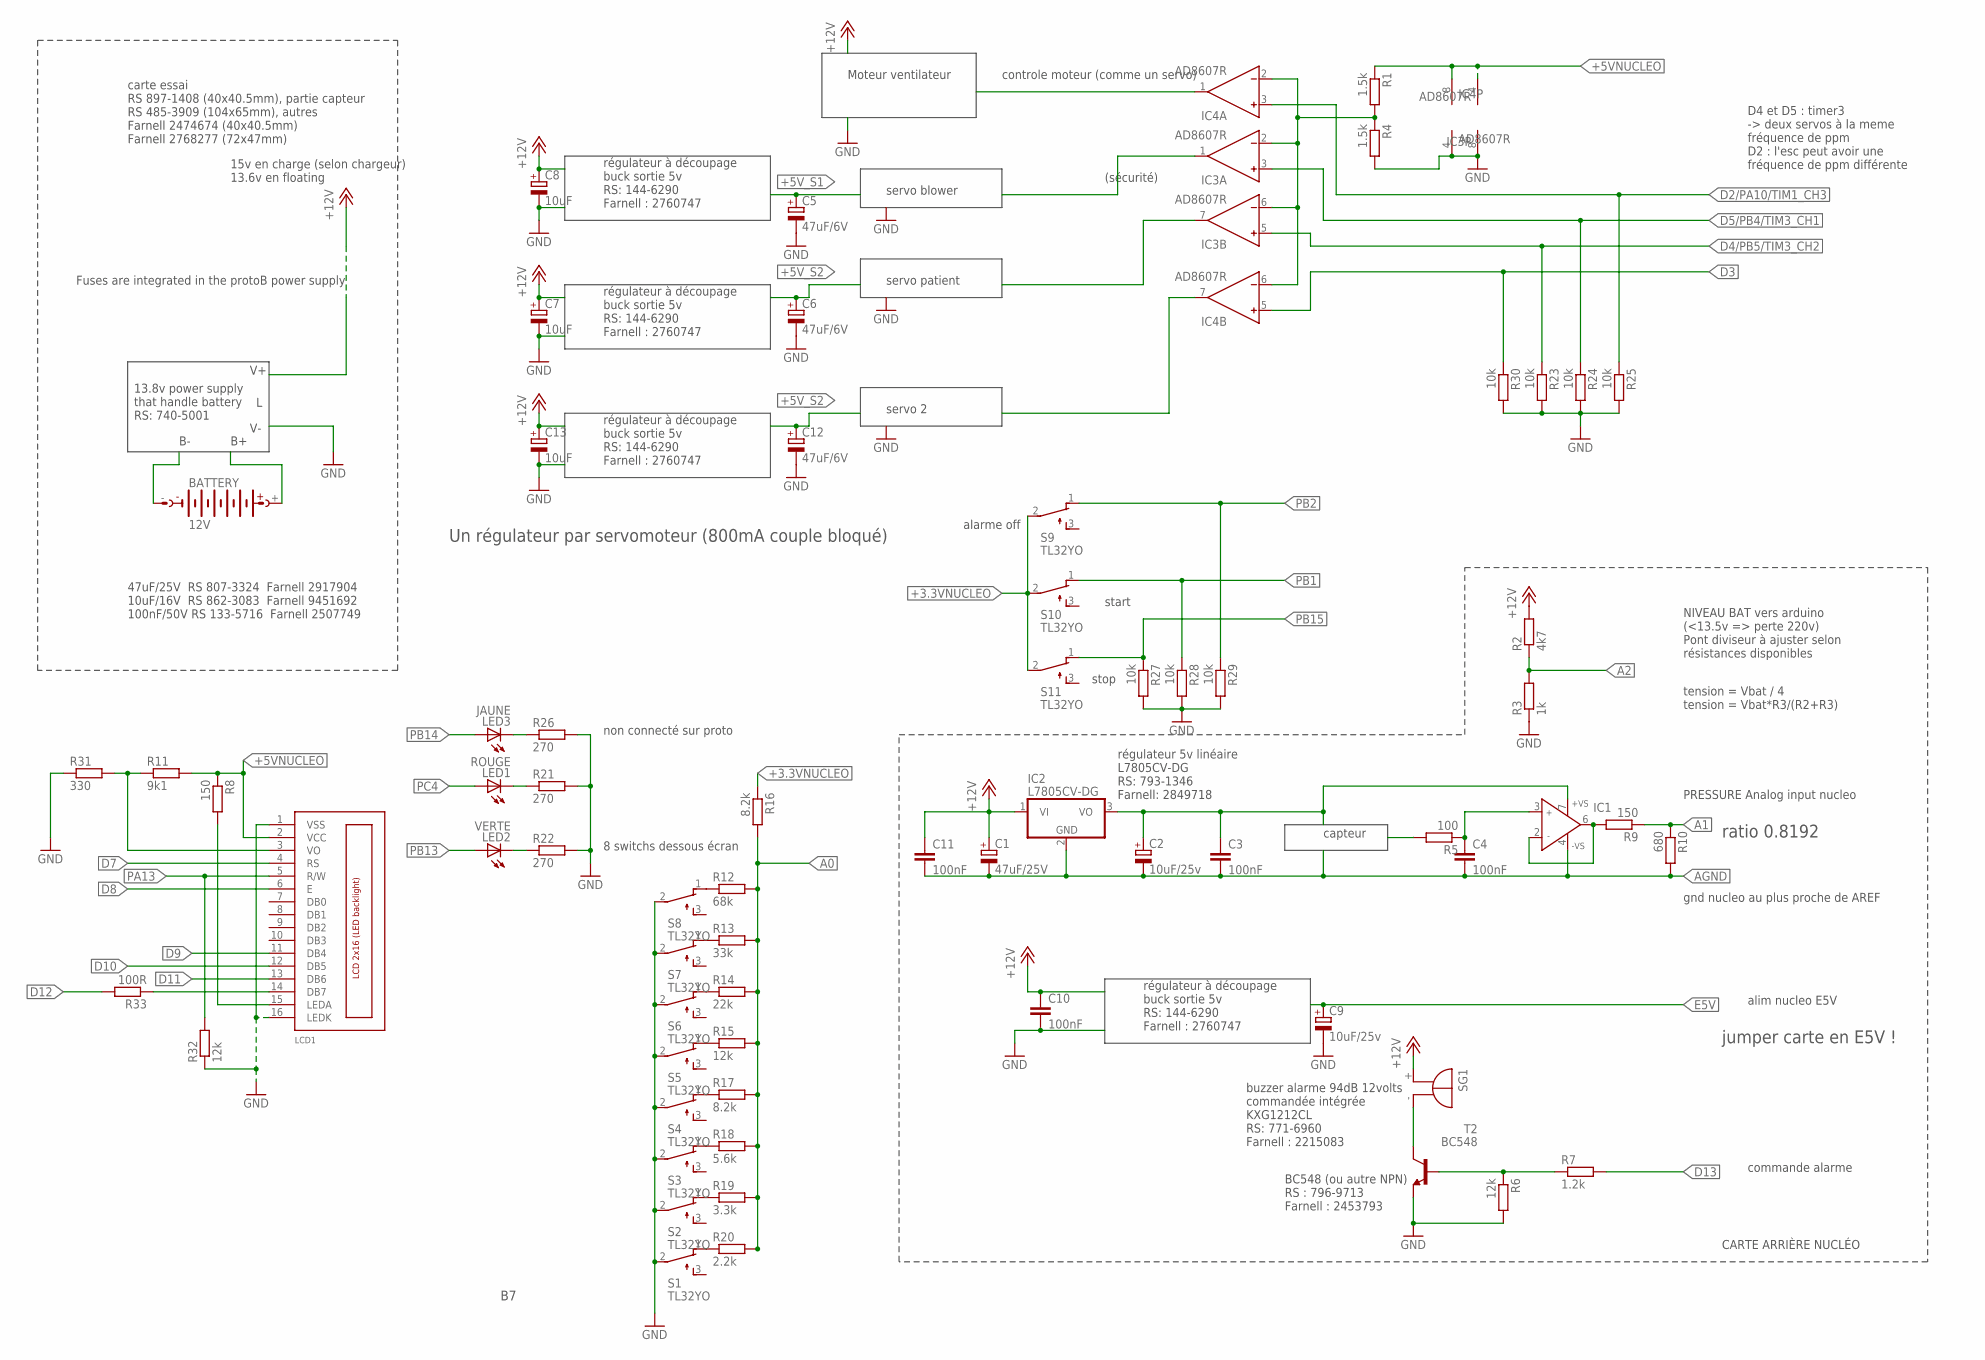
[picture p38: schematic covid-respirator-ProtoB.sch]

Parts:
BATTERY: 12V; AB9V
C1: 47uF/25V; 150CLZ-1010
C2, C9: 10uF/25v; 150CLZ-1010
C3, C4, C10, C11: 100nF; C050-050X075
C5, C6, C12: 47uF/6V; 150CLZ-1010
C7, C8, C13: 10uF; 150CLZ-1010
IC1: AD825R; SO8
IC2: L7805CV-DG; TO220H
IC3, IC4: AD8607R; SO8
LCD1: LCD_2X16_SIL; HY-1602F
LED1: ROUGE; LED3MM
LED2: VERTE; LED3MM
LED3: JAUNE; LED3MM
R1, R4: 1.5k; 0207/10
R2: 4k7; 0207/10
R3: 1k; 0207/10
R5: 100; 0207/10
R6, R15, R32: 12k; 0207/10
R7: 1.2k; 0207/10
R8, R9: 150; 0207/10
R10: 680; 0207/10
R11: 9k1; 0207/10
R12: 68k; 0207/10
R13: 33k; 0207/10
R14: 22k; 0207/10
R16, R17: 8.2k; 0207/10
R18: 5.6k; 0207/10
R19: 3.3k; 0207/10
R20: 2.2k; 0207/10
R21, R22, R26: 270; 0207/10
R23, R24, R25, R27, R28, R29, R30: 10k; 0207/10
R31: 330; 0207/10
R33: 100R; 0207/10
S1, S2, S3, S4, S5, S6, S7, S8, S9, S10, S11: TL32YO; TL3XYO
SG1: F/EB20P
T2: BC548; TO92-CBE

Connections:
6546876: C4.1, IC1.3 (IN+), R5.1
+3.3VNUCLEO: R16.1, S9.2, S10.2, S11.2
+5VNUCLEO: IC3.4 (V-), IC4.8 (V+), LCD1.2 (VCC), R1.1, R8.1, R11.2
+5V_S1: C5.+
+5V_S2: C6.+, C12.+
+12V: C1.+, C7.+, C8.+, C10.1, C11.1, C13.+, IC2.1 (VI), R2.2, SG1.+
A0: R12.2, R13.2, R14.2, R15.2, R16.2, R17.2, R18.2, R19.2, R20.2
A1: R9.1, R10.1
A2: R2.1, R3.2
AGND: C1.-, C2.-, C3.2, C4.2, C11.2, IC1.4 (-VS), IC2.2 (GND), R10.2
AREF: C2.+, C3.1, IC1.7 (+VS), IC2.3 (VO)
D2: IC3.3 (IN+), R24.1
D3: IC4.5 (IN+), R30.1
D4: IC3.5 (IN+), R23.1
D5: IC4.3 (IN+), R25.1
D7: LCD1.4 (RS)
D8: LCD1.6 (E)
D9: LCD1.11 (DB4)
D10: LCD1.12 (DB5)
D11: LCD1.13 (DB6)
D12: R33.2
D13: R7.2
E5V: C9.+
GND: C5.-, C6.-, C7.-, C8.-, C9.-, C10.2, C12.-, C13.-, IC3.8 (V+), IC4.4 (V-), LCD1.1 (VSS), LCD1.16 (LEDK), R3.1, R4.2, R6.2, R21.2, R22.2, R23.2, R24.2, R25.2, R26.2, R27.2, R28.2, R29.2, R30.2, R31.1, R32.1, S1.2, S2.2, S3.2, S4.2, S5.2, S6.2, S7.2, S8.2, T2.E
unnamed: IC3.2 (IN-), IC3.6 (IN-), IC4.2 (IN-), IC4.6 (IN-), R1.2, R4.1
unnamed: LCD1.15 (LEDA), R8.2
unnamed: IC1.2 (IN-), IC1.6 (OUT), R9.2
unnamed: LCD1.3 (VO), R11.1, R31.2
unnamed: R12.1, S8.1 (O)
unnamed: SG1.-, T2.C
unnamed: R6.1, R7.1, T2.B
unnamed: R13.1, S7.1 (O)
unnamed: R14.1, S6.1 (O)
unnamed: R15.1, S5.1 (O)
unnamed: R17.1, S4.1 (O)
unnamed: R18.1, S3.1 (O)
unnamed: R19.1, S2.1 (O)
unnamed: R20.1, S1.1 (O)
unnamed: LED3.K (C), R26.1
unnamed: LED1.K (C), R21.1
unnamed: LED2.K (C), R22.1
unnamed: LCD1.14 (DB7), R33.1
PA13: LCD1.5 (R/W), R32.2
PB1: R28.1, S10.1 (O)
PB2: R29.1, S9.1 (O)
PB13: LED2.A
PB14: LED3.A
PB15: R27.1, S11.1 (O)
PC4: LED1.A

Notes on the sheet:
Moteur ventilateur
controle moteur (comme un servo)
(sécurité)
NIVEAU BAT vers arduino (<13.5v => perte 220v) Pont diviseur à ajuster selon résistances disponibles
tension = Vbat / 4 tension = Vbat*R3/(R2+R3)
15v en charge (selon chargeur) 13.6v en floating
capteur
PRESSURE Analog input nucleo
gnd nucleo au plus proche de AREF
régulateur à découpage buck sortie 5v RS: 144-6290 Farnell : 2760747
alim nucleo E5V
régulateur 5v linéaire L7805CV-DG RS: 793-1346 Farnell: 2849718
buzzer alarme 94dB 12volts commandée intégrée KXG1212CL RS: 771-6960 Farnell : 2215083
BC548 (ou autre NPN) RS : 796-9713 Farnell : 2453793
CARTE ARRIÈRE NUCLÉO
carte essai RS 897-1408 (40x40.5mm), partie capteur RS 485-3909 (104x65mm), autres Farnell 2474674 (40x40.5mm) Farnell 2768277 (72x47mm)
47uF/25V RS 807-3324 Farnell 2917904 10uF/16V RS 862-3083 Farnell 9451692 100nF/50V RS 133-5716 Farnell 2507749
13.8v power supply that handle battery RS: 740-5001
Un régulateur par servomoteur (800mA couple bloqué)
ratio 0.8192
jumper carte en E5V !
commande alarme
Fuses are integrated in the protoB power supply
servo blower
servo patient
8 switchs dessous écran
non connecté sur proto
alarme off
start
stop
servo 2
D4 et D5 : timer3 -> deux servos à la meme fréquence de ppm D2 : l'esc peut avoir une fréquence de ppm différente

Board: 2 copper layers, 68 parts (0 on the bottom side), 37 nets, no tracks yet.

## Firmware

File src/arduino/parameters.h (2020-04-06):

/*
    Copyright (C) 2020 Makers For Life
*/
/******************************************************************************
 * @author Makers For Life
 * @file parameters.h
 * @brief Various settings
 *****************************************************************************/
#pragma once

// INCLUDES ===================================================================

// External
#include <Arduino.h>

// Internal
#include "config.h"

// PARAMETERS =================================================================

/// Current version of the software
#define VERSION "v1.1.45"

/**
 * @name Core parameters
 */
///@{

// Période de traitement en millisecondes
#define PCONTROLLER_COMPUTE_PERIOD 10

// Minimums et maximums possible des paramètres modifiables à l'exécution
#define BORNE_SUP_PRESSION_CRETE 700    // arbitraire [mmH2O]
#define BORNE_INF_PRESSION_CRETE 100    // arbitraire [mmH2O]
#define BORNE_SUP_PRESSION_PLATEAU 400  // PP MAX SDRA = 300 [mmH2O]
#define BORNE_INF_PRESSION_PLATEAU 100  // arbitraire [mmH2O]
#define BORNE_SUP_PRESSION_PEP 300      // PP MAX = 300, or PEP < PP [mmH2O]
#define BORNE_INF_PRESSION_PEP 50       // arbitraire mais > 0 [mmH2O]
#define INITIAL_ZERO_PRESSURE 0         // [mmH2O]

#define DEFAULT_MIN_PEEP_COMMAND 80
#define DEFAULT_MAX_PLATEAU_COMMAND 300
#define DEFAULT_MAX_PEAK_PRESSURE_COMMAND 320

#define INITIAL_CYCLE_NB 20
#define BORNE_SUP_CYCLE 35  // demande medical
#define BORNE_INF_CYCLE 5   // demande medical

///@}

/**
 * @name PID gains & settings
 */
///@{
static const int32_t PID_BLOWER_KP = 4;
static const int32_t PID_BLOWER_KI = 32;
static const int32_t PID_BLOWER_KD = 4;

static const int32_t PID_BLOWER_INTEGRAL_MAX = 1000;
static const int32_t PID_BLOWER_INTEGRAL_MIN = -1000;

static const int32_t PID_PATIENT_KP = 64;
static const int32_t PID_PATIENT_KI = 100;
static const int32_t PID_PATIENT_KD = 4;

static const int32_t PID_PATIENT_INTEGRAL_MAX = 1000;
static const int32_t PID_PATIENT_INTEGRAL_MIN = -1000;
///@}

/**
 * @name Valves
 */
///@{

/// Angle when open
#define VALVE_OUVERT 25

/// Angle when closed
#define VALVE_FERME 145

#define SERVO_VALVE_PERIOD 20000
#define PIN_SERVO_BLOWER D2  // PA10 / TIM1_CH3
#define TIM_CHANNEL_SERVO_VALVE_BLOWER 3
#define PIN_SERVO_PATIENT D4  // PB5 / TIM3_CH2
#define TIM_CHANNEL_SERVO_VALVE_PATIENT 2

///@}

/**
 * @name LCD screen
 */
///@{

#define PIN_LCD_RS D7
#define PIN_LCD_RW PA13
#define PIN_LCD_EN D8
#define PIN_LCD_D4 D9
#define PIN_LCD_D5 D10
#define PIN_LCD_D6 D11
#define PIN_LCD_D7 D12

/// Number of lines
#define SCREEN_LINE_NUMBER 4

/// Number of characters per line
#define SCREEN_LINE_LENGTH 20

/// Period between screen updates in hundredth of second
#define LCD_UPDATE_PERIOD 20

///@}

/**
 * @name Buttons
 */
///@{

#define PIN_CONTROL_BUTTONS A0
#define PIN_BTN_ALARM_OFF PB2
#define PIN_BTN_START PB1
#define PIN_BTN_STOP PB15
#define TENSION_BTN_PRESSION_P_CRETE_PLUS 913
#define TENSION_BTN_PRESSION_P_CRETE_MINUS 819
#define TENSION_BTN_PRESSION_PLATEAU_PLUS 745
#define TENSION_BTN_PRESSION_PLATEAU_MINUS 608
#define TENSION_BTN_PEP_PLUS 512
#define TENSION_BTN_PEP_MINUS 415
#define TENSION_BTN_CYCLE_PLUS 294
#define TENSION_BTN_CYCLE_MINUS 216

///@}

/**
 * @name Other I/O
 */
///@{

#define PIN_CAPTEUR_PRESSION A1
#define PIN_ALARM D13
#define PIN_LED_RED PC4
#define PIN_LED_GREEN PB13
#define PIN_LED_YELLOW PB14
#define PIN_ESC_BLOWER D5  // PB4 / TIM3_CH1
#define TIM_CHANNEL_ESC_BLOWER 1
#define PIN_BATTERY A2

///@}

// USELESS?

// amplitude radiale des servomoteurs
// \warning ANGLE_FERMETURE has to be greater than ANGLE_OUVERTURE_MAXI
static const uint16_t ANGLE_OUVERTURE_MINI = 8;
static const uint16_t ANGLE_OUVERTURE_MAXI = 45;
static const uint16_t ANGLE_FERMETURE = 90;

// multiplicateur à modifier pour inverser les angles (en cas de suppression de
// l'engrenage)
static const int16_t ANGLE_MULTIPLICATEUR = 1;

// borne pour le capteur de pression
// a adapter lors de la calibration
static const uint16_t CAPT_PRESSION_MINI = 0;

// on ne va pas jusqu'à 1024 à cause de la saturation de l'AOP
// -> à adapter avec meilleur AOP
static const uint16_t CAPT_PRESSION_MAXI = 800;

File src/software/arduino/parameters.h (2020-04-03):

/*=============================================================================
 * @file parameters.h
 *
 * COVID Respirator
 *
 * @section copyright Copyright
 *
 * Makers For Life
 *
 * @section descr File description
 *
 * This file defines the Makair parameters
 */

#pragma once

// INCLUDES ===================================================================

// External
#include <AnalogButtons.h>
#include <Arduino.h>
#include <LiquidCrystal.h>

// Internal
#include "config.h"

// STRUCTURES =================================================================

/*! This enum lists the different screen sizes
 *  2 LCD versions are supported:
 *  -   LCD with 16 columns and 2 rows (16x2)
 *  -   LCD with 20 columns and 4 rows (20x4)
 */
enum ScreenSize
{
    CHARS_16,
    CHARS_20
};

// PARAMETERS =================================================================

// amplitude radiale des servomoteurs
// \warning ANGLE_FERMETURE has to be greater than ANGLE_OUVERTURE_MAXI
static const uint16_t ANGLE_OUVERTURE_MINI = 8;
static const uint16_t ANGLE_OUVERTURE_MAXI = 45;
static const uint16_t ANGLE_FERMETURE = 90;

// multiplicateur à modifier pour inverser les angles (en cas de suppression de
// l'engrenage)
static const int16_t ANGLE_MULTIPLICATEUR = 1;

// borne pour le capteur de pression
// a adapter lors de la calibration
static const uint16_t CAPT_PRESSION_MINI = 0;

// on ne va pas jusqu'à 1024 à cause de la saturation de l'AOP
// -> à adapter avec meilleur AOP
static const uint16_t CAPT_PRESSION_MAXI = 800;

#define VERSION "v1.1.41"
#define BLOWER_OUVERT 25
#define BLOWER_DEMI_OUVERT 90
#define BLOWER_FERME 150
#define PATIENT_OUVERT 25
#define PATIENT_FERME 150

#define SERVO_VALVE_PERIOD 20000

#define PIN_CAPTEUR_PRESSION A1
#define PIN_ALARM D13
#define PIN_LED_RED PC4
#define PIN_LED_GREEN PB13
#define PIN_LED_YELLOW PB14
#define PIN_ESC_BLOWER D5 // PB4 / TIM3_CH1
#define TIM_CHANNEL_ESC_BLOWER 1
#define PIN_SERVO_BLOWER D2 // PA10 / TIM1_CH3
#define TIM_CHANNEL_SERVO_VALVE_BLOWER 3
#define PIN_SERVO_PATIENT D4 // PB5 / TIM3_CH2
#define TIM_CHANNEL_SERVO_VALVE_PATIENT 2
#define PIN_CONTROL_BUTTONS A0
#define PIN_BATTERY A2
#define PIN_BTN_ALARM_OFF PB2
#define PIN_BTN_START PB1
#define PIN_BTN_STOP PB15
/* Ecran LCD */
#define PIN_LCD_RS D7
#define PIN_LCD_RW PA13
#define PIN_LCD_EN D8
#define PIN_LCD_D4 D9
#define PIN_LCD_D5 D10
#define PIN_LCD_D6 D11
#define PIN_LCD_D7 D12

// contrôle de l'écran LCD
static const ScreenSize screenSize{ScreenSize::CHARS_20};
// période (en centièmes de secondes) de mise à jour du feedback des
// consignes sur le LCD
static const int16_t LCD_UPDATE_PERIOD = 20;

// Periode de traitement en millisecondes
static const uint32_t PCONTROLLER_COMPUTE_PERIOD = 10;

// minimums et maximums possible des paramètres modifiables à l'exécution
static const uint16_t BORNE_SUP_PRESSION_CRETE = 700;   // arbitraire [mmH2O]
static const uint16_t BORNE_INF_PRESSION_CRETE = 100;   // arbitraire [mmH2O]
static const uint16_t BORNE_SUP_PRESSION_PLATEAU = 400; // PP MAX SDRA = 300 [mmH2O]
static const uint16_t BORNE_INF_PRESSION_PLATEAU = 100; // arbitraire [mmH2O]
static const uint16_t BORNE_SUP_PRESSION_PEP = 300;     // PP MAX = 300, or PEP < PP [mmH2O]
static const uint16_t BORNE_INF_PRESSION_PEP = 50;      // arbitraire mais > 0 [mmH2O]
static const uint16_t INITIAL_ZERO_PRESSURE = 0;        // [mmH2O]

static const uint16_t DEFAULT_MIN_PEEP_COMMAND = 50;
static const uint16_t DEFAULT_MAX_PLATEAU_COMMAND = 150;
static const uint16_t DEFAULT_MAX_PEAK_PRESSURE_COMMAND = 200;

static const uint16_t INITIAL_CYCLE_NB = 20;
static const uint16_t BORNE_SUP_CYCLE = 35; // demande medical
static const uint16_t BORNE_INF_CYCLE = 5;  // demande medical

static const uint16_t TENSION_BTN_PRESSION_P_CRETE_PLUS = 913;
static const uint16_t TENSION_BTN_PRESSION_P_CRETE_MINUS = 819;
static const uint16_t TENSION_BTN_PRESSION_PLATEAU_PLUS = 745;
static const uint16_t TENSION_BTN_PRESSION_PLATEAU_MINUS = 608;
static const uint16_t TENSION_BTN_PEP_PLUS = 512;
static const uint16_t TENSION_BTN_PEP_MINUS = 415;
static const uint16_t TENSION_BTN_CYCLE_PLUS = 294;
static const uint16_t TENSION_BTN_CYCLE_MINUS = 216;

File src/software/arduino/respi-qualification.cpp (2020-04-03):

/*=============================================================================
 * @file respi-tests.h
 *
 * COVID Respirator
 *
 * @section copyright Copyright
 *
 * Makers For Life
 *
 * @section descr File description
 *
 * This file execute the MakAir test program
 */

#pragma once

#include "config.h"
#if MODE == MODE_QUALIFICATION

// INCLUDES ===================================================================

// External
#include <Arduino.h>
#include <OneButton.h>

// Internal
#include "affichage.h"
#include "air_transistor.h"
#include "common.h"
#include "debug.h"
#include "parameters.h"
#include "pression.h"

/**
 * Liste de toutes les étapes de test du montage.
 */
#define STEP_LCD 1
#define STEP_WELCOME 2
#define STEP_BTN_PRESSION_CRETE_PLUS 3
#define STEP_BTN_PRESSION_CRETE_MINUS 4
#define STEP_BTN_PRESSION_PLATEAU_PLUS 5
#define STEP_BTN_PRESSION_PLATEAU_MINUS 6
#define STEP_BTN_PEP_PLUS 7
#define STEP_BTN_PEP_MINUS 8
#define STEP_BTN_CYCLE_PLUS 9
#define STEP_BTN_CYCLE_MINUS 10
#define STEP_BTN_ALARM_OFF 11
#define STEP_BTN_START 12
#define STEP_BTN_STOP 13
#define STEP_LED_RED 14
#define STEP_LED_YELLOW 15
#define STEP_LED_GREEN 16
#define STEP_ALARM 17
#define STEP_SERVO_BLOWER_OPEN 18
#define STEP_SERVO_BLOWER_CLOSE 19
#define STEP_SERVO_PATIENT_OPEN 20
#define STEP_SERVO_PATIENT_CLOSE 21
#define STEP_SERVOS 22
#define STEP_BLOWER 23
#define STEP_PRESSURE_EMPTY 24
#define STEP_PRESSURE_VAL1 25
#define STEP_PRESSURE_VAL2 26
#define STEP_PRESSURE_VAL3 27
#define STEP_DONE 28

static uint8_t step = STEP_LCD;

static uint8_t is_drawn = false;
#define UNGREEDY(is_drawn, statement) if (is_drawn == 0) { statement; is_drawn = 1; }

void changeStep(uint8_t new_step) {
    step = new_step;
    is_drawn = 0;
}

static uint8_t errors = 0;

#define PRESSURE_MARGIN_PER_CENT 5
#define PRESSURE_EMPTY_MARGIN 5 // [mmH2O]
#define PRESSURE_EMPTY 0 // [mmH2O]
#define PRESSURE_VAL1 700 // [mmH2O]
#define PRESSURE_VAL2 150 // [mmH2O]
#define PRESSURE_VAL3 300 // [mmH2O]

bool isPressureValueGoodEnough(int expected, int pressure) {
    int epsylon = expected * PRESSURE_MARGIN_PER_CENT / 100;
    return (pressure >= (expected - epsylon)) && (pressure <= (expected + epsylon));
}

/**
 * Affiche un pattern de la forme suivante sur l'écran LCD.
 * La taille du pattern s'adapte en fonction du nombre de ligne et
 * de caractères de l'écran LCD.
 *
 * 01234567890123456789
 * 12345678901234567890
 * 23456789012345678901
 * 34567890123456789012
 */
void displayTestPattern()
{
    uint8_t line_number;
    uint8_t line_length;
    switch (screenSize)
    {
    case ScreenSize::CHARS_20:
    {
        line_number = 4;
        line_length = 20;
        break;
    }
    default:
    {
        line_number = 2;
        line_length = 16;
    }
    }

    for (int line = 0; line < line_number; line++)
    {
        screen.setCursor(0, line);
        for (int character = 0; character < line_length; character++)
        {
            screen.print((character + line) % 10);
        }
    }
}

//! This function displays 2 lines of 16 characters (or less)
void display(char line1[], char line2[]) {
    resetScreen();
    screen.setCursor(0, 0);
    screen.print(line1);
    screen.setCursor(0, 1);
    screen.print(line2);
}

//! This function displays only adds a status message in the 4th line
void displayStatus(char msg[], uint8_t line = 3) {
    screen.setCursor(0, line);
    screen.print("                    ");
    screen.setCursor(0, line);
    screen.print(msg);
}

AirTransistor servoBlower;
AirTransistor servoPatient;
HardwareTimer* hardwareTimer1;
HardwareTimer* hardwareTimer3;

void onPressionCretePlusClick()
{
    DBG_DO(Serial.println("pression crete ++"));
    if (step == STEP_LCD || step == STEP_WELCOME) {
        changeStep(step + 1);
    } else if (step == STEP_BTN_PRESSION_CRETE_PLUS) {
        changeStep(step + 1);
    } else if (step == STEP_SERVO_BLOWER_OPEN) {
        changeStep(step + 1);
    } else if (step != STEP_DONE) {
        displayStatus("WRONG BUTTON PUSHED");
        errors++;
    }
}

void onPressionCreteMinusClick()
{
    DBG_DO(Serial.println("pression crete --"));
    if (step == STEP_LCD || step == STEP_WELCOME) {
        changeStep(step + 1);
    } else if (step == STEP_BTN_PRESSION_CRETE_MINUS) {
        changeStep(step + 1);
    } else if (step == STEP_SERVO_BLOWER_CLOSE) {
        changeStep(step + 1);
    } else if (step != STEP_DONE) {
        displayStatus("WRONG BUTTON PUSHED");
        errors++;
    }
}

void onPressionPlateauPlusClick()
{
    DBG_DO(Serial.println("pression plateau ++"));
    if (step == STEP_LCD || step == STEP_WELCOME) {
        changeStep(step + 1);
    } else if (step == STEP_BTN_PRESSION_PLATEAU_PLUS) {
        changeStep(step + 1);
    } else if (step == STEP_SERVO_PATIENT_OPEN) {
        changeStep(step + 1);
    } else if (step != STEP_DONE) {
        displayStatus("WRONG BUTTON PUSHED");
        errors++;
    }
}

void onPressionPlateauMinusClick()
{
    DBG_DO(Serial.println("pression plateau --"));
    if (step == STEP_LCD || step == STEP_WELCOME) {
        changeStep(step + 1);
    } else if (step == STEP_BTN_PRESSION_PLATEAU_MINUS) {
        changeStep(step + 1);
    } else if (step == STEP_SERVO_PATIENT_CLOSE) {
        changeStep(step + 1);
    } else if (step != STEP_DONE) {
        displayStatus("WRONG BUTTON PUSHED");
        errors++;
    }
}

void onPepPlusClick()
{
    DBG_DO(Serial.println("pression pep ++"));
    if (step == STEP_LCD || step == STEP_WELCOME) {
        changeStep(step + 1);
    } else if (step == STEP_BTN_PEP_PLUS) {
        changeStep(step + 1);
    } else if (step == STEP_SERVOS) {
        changeStep(step + 1);
    } else if (step != STEP_DONE) {
        displayStatus("WRONG BUTTON PUSHED");
        errors++;
    }
}

void onPepMinusClick()
{
    DBG_DO(Serial.println("pression pep --"));
    if (step == STEP_LCD || step == STEP_WELCOME) {
        changeStep(step + 1);
    } else if (step == STEP_BTN_PEP_MINUS) {
        changeStep(step + 1);
    } else if (step == STEP_BLOWER) {
        hardwareTimer3->setCaptureCompare(TIM_CHANNEL_ESC_BLOWER, Angle2MicroSeconds(0), MICROSEC_COMPARE_FORMAT);
        changeStep(step + 1);
    } else if (step != STEP_DONE) {
        displayStatus("WRONG BUTTON PUSHED");
        errors++;
    }
}
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

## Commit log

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2020-03-25 Step filter_box_V2
    [SCREW_M3_25_box filter25032020.STEP, SCREW_M3_30 _box filter25032020.STEP, brake nut_box filter25032020.STEP, buttom_box filter25032020.STEP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]
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2020-03-25 Re-organize filter box V2 files
    [Assemblage_free_box filter25032020.SLDASM, Bottom case.step, Bottom case.stl, Joint.step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]
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2020-03-26 Housing v2
    [housing V2.stl]
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2020-03-26 Pressure Valve, V2
    [Cale_reglage_1mm.stl, Cale_reglage_2mm.stl, Core.stl, Equerre_valve_clapet.stl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]
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2020-03-26 Created venturi valve for FiO2 30%
    [Respirator-free reanimation Venturi's valve (rev. 4) FiO2-28 Body.STEP, Respirator-free reanimation Venturi's valve (rev. 4) FiO2-28 Body.STL, Respirator-free 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]
2020-03-26 Bump PV
    [Pressure Valve.f3d, Shutter.stl]
2020-03-27 Renamed folder & put new venturi valve in place
    [Oxygen Mixer V1.f3d, cap_FiO2_30_v1.step, cap_FiO2_30_v1.stl]
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2020-03-27 Add 2WV initial files
    [Two Way Valve.f3d, Valve.stl]
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2020-03-27 Bump 2WV
    [Two Way Valve.f3d]
2020-03-27 Bump w/ Michelin suggestions
    [Air Transistor V4.f3d]
2020-03-27 update protoB schematic
    [covid-respirator-ProtoB.brd, covid-respirator-ProtoB.sch]
2020-03-27 V3 filterbox
    first version of the filter box with a screwing pitch
    [bottom_fliter_box v3.STEP, bottom_fliter_box v3.STL, fliter_box ring top bottom_v3.SLDPRT, ring_fliter_box v3 .STL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]
2020-03-27 Renamed files to properly match v2
    [Respirator-free reanimation Venturi's valve (rev. 4) FiO2-28 Body.STEP, Respirator-free reanimation Venturi's valve (rev. 4) FiO2-28 Body.STL, Respirator-free 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]
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2020-03-27 Optimize 2WV for FDM printing (supportless, at most)
    [Tube Fit Bottom.stl, Tube Fit Top.stl, Two Way Valve.f3d]
2020-03-27 add filter_box V4
    [Assemblage_fliber_box v4.STEP, butttom v4.STL, fliter_box v4 02.SLDPRT, ring_fliter_box v4 .STL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]
2020-03-27 Cleanup filter-box V3 and V4
    Kudos to Martial Medjber
    [bottom_filter_box v3.STEP, bottom_filter_box_v3.STL, bottom_filter_box_v4.STL, filter_box_v3.SLDPRT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]
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2020-03-27 Add pressure-valve and 2wv STEP files
    [(Unsaved).step]
2020-03-27 Rename STEP files
    [pressure-valve.step, two_way_valve.step]
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2020-03-28 Fixes on 2WV for elastomers printability
    [One-Way Gate Bottom.stl, One-Way Gate Top.stl, Tube Fit Bottom.stl, Two Way Valve.f3d]
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2020-03-28 Bump PV for support-less FDM printing
    [Core.stl, Pressure Valve.f3d]
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2020-03-28 Improve AT V4 servo fit
    [Air Transistor V4.f3d, Motor Casing.stl]
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2020-03-28 New & simpler design, CFD simulation, ready for printing
    Simpler valve for easy printing on FDM
    Higher structural strength (min 2mm wall thickness)
    FiO2 validated through CFD simulation
    Ready to print
    [cap_FiO2_30_v2.step, cap_FiO2_30_v2.stl, oxygen_mixer_v3.f3d, oxygen_mixer_v3.step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]
2020-03-28 Corrected model to reach 19mm OD
    Messed up, don't ask :D
    [oxygen_mixer_v3.f3d, oxygen_mixer_v3.step, oxygen_mixer_v3.stl]
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2020-03-30 schematic B5
    [covid-respirator-ProtoB.brd, covid-respirator-ProtoB.sch]
2020-03-30 Filter Box V5 (concept)
    [Basis.stl, Filter Box V0.f3d, Filter Box V1.f3d, Filter Box V5.f3d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]
2020-03-30 schematic B6 with servo names
    [covid-respirator-ProtoB.sch]
2020-03-30 Updated to 6mm ID O2 line
    [oxygen_mixer_v4.f3d, oxygen_mixer_v4.step, oxygen_mixer_v4.stl]
2020-03-30 Bump FB
    [Basis.stl, Filter Box V5.f3d, Joint.stl, Seal.stl]
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2020-04-01 Suppression fichiers binaires
    [analyse-phase-sous-phase.ods, out.csv]
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2020-04-01 Initiate Git cleanup
    [Adapter 15-15.step, Adapter 15-15.stl, Adapter Validation Compressor Pump 11mm to 15mm.f3d, Adapter Validation Compressor Pump 11mm to 15mm.stl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]
2020-04-01 Import filter variants
    [Basis.stl, Joint.stl, Machine Filter Box V1 (Intake).f3d, Machine Filter Box V1 (Outtake).f3d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]
2020-04-01 Add filter box V5, injection molding variant
    [Filter Box v5.step]
2020-04-01 Add patient-filter-box V5 files
    [Assemblage_Filter Box v5 02 for 3D print.STEP, buttom_Filter Box v5 02 for 3D print.STEP, ring_Filter Box v5 02 for 3D print.STEP, top_Filter Box v5 02 for 3D 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]
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2020-04-02 Bump filter outtake
    [Basis.stl, Machine Filter Box V1 (Outtake).f3d]
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2020-04-02 Bump Filter Boxes
    [Machine Filter Box V1 (Intake).f3d, Machine Filter Box V1 (Outtake).f3d, Seal.stl]
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2020-04-02 Split = Bump Filter Box variants
    [Basis.stl, Filter Box V5 (Intake Variant).f3d, Machine Filter Box V1 (Intake).f3d, Seal.stl]
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2020-04-02 Add blower-holder
    [blower_holder_body.stl, blower_holder_bottom.stl, blower_holder_top.stl]
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2020-04-02 Add Blower casing
    [Blower - Duct.stl, Blower - Propeller.stl, Blower - Top.stl, Blower Casing.f3d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]
2020-04-02 Archived adapters
    [Adapter Validation Compressor Pump 11mm to 15mm.f3d, Adapter Validation Compressor Pump 11mm to 15mm.stl, Adapter Validation Lung to 15mm.f3d, Adapter Validati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]
2020-04-02 Import all blower holder parts
    [Blower Holder Casing.f3d, Blower Holder Core.f3d, Body.stl, Top.stl]
2020-04-02 Import oxygen filter render
    [Body.step, Body.stl, Oxygen Mixer V3.f3d, Oxygen Mixer V4.f3d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]
2020-04-02 Import bodies
    [Body 1.stl, Body 2.stl]
2020-04-02 Add all pneumatic connectors
    [pneumatic-connector-blower-v4.f3d, pneumatic-connector-blower-v4.step, pneumatic-connector-blower-v4.stl, pneumatic-connector-o2-V3 v1.step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]
2020-04-02 Add Pressure Valve V3 STEP file
    [Ass_Montage_Excentrique_Small_palonnier_SKF_V3.STEP]
2020-04-02 Update Pneumatic Connector Respiratory Pressure
    [pneumatic-connector-respiratory-pressure v1.step, pneumatic-connector-respiratory-pressure v1.stl, pneumatic-connector-respiratory-pressure.f3d]
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2020-04-02 Refactor Pressure Valve
    [Pressure Valve V3.step]
2020-04-02 Import STL
    [Axis Rotation Fit.stl, Servo Fit Axis.stl, Servo Fit.stl, Servo Locker.stl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]
2020-04-02 change timer order to have timer3 for both servos
    [covid-respirator-ProtoB.sch]
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2020-04-03 Bump OM
    [Body.stl, Oxygen Mixer V4.f3d]
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2020-04-03 Update oxygen mixer V4
    [Body.step]
2020-04-03 Classified oxygen-mixer V5 as experimental
    [Body 1.stl, Body 2.stl, Oxygen Mixer V5-experimental.f3d]
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2020-04-03 Improvements to Outtake Machine Filter
    [Basis.stl, Machine Filter Box V1 (Intake).f3d, Machine Filter Box V1 (Intake).step, Machine Filter Box V1 (Outtake).f3d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]
2020-04-03 Refactor CAD naming conventions
    [Adapter Validation Compressor Pump 11mm to 15mm.f3d, Adapter Validation Lung to 15mm.f3d, Air Transistor V1.f3d, Air Transistor V2.f3d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]
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2020-04-03 Export Blower Holder as STEP
    [Blower Holder Casing.step, Blower Holder Core.step]
2020-04-03 Refactor Blower tree + Export V9 STL
    [Blower - Duct.stl, Blower - Propeller.stl, Blower - Top.stl, Blower V1.f3d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]
2020-04-03 Re-classify soft + mechs
    [Adapter 15-15.step, Adapter 15-15.stl, Adapter Validation Compressor Pump 11mm to 15mm.f3d, Adapter Validation Compressor Pump 11mm to 15mm.stl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]
2020-04-03 Re-clasify files
    [Adapter 15-15.step, Adapter 15-15.stl, Adapter Validation Compressor Pump 11mm to 15mm.f3d, Adapter Validation Compressor Pump 11mm to 15mm.stl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]
2020-04-03 Re-order electronics
    [covid-respirator-ProtoB.brd, covid-respirator-ProtoB.sch, respi_V0.fzz]
2020-04-03 Refactor mechanics tree
    [Adapter 15-15.step, Adapter 15-15.stl, Adapter Validation Compressor Pump 11mm to 15mm.f3d, Adapter Validation Compressor Pump 11mm to 15mm.stl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]
2020-04-03 Normalize all mechanics paths + tree structures
    [Assemblage_free_box filter25032020.SLDASM, Basis.stl, Blower Holder V1 - Casing.f3d, Blower Holder V1 - Casing.step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]
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2020-04-03 Filter Box V5.3
    [Assemblage_Filter Box v5 02 for 3D print.STEP, Bottom case.step, Bottom case.stl, Bottom.stl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]
2020-04-03 Add CAD live view linls
    [Pressure Valve V4.step, Pressure Valve V5.step]
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2020-04-03 Add patient-filter-box V6
    [Bottom Filter Box V6.STEP, Bottom.STL, Bottom.stl, Filter Box V5.f3d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]
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2020-04-03 Add patient-filter-box F360
    [Bottom Filter Box V6.STEP, Patient Filter Box V6 - Bottom.STEP, Patient Filter Box V6 - Top.STEP, Patient Filter Box V6.STEP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]
2020-04-04 Add container V2
    [Container v2.f3d]
2020-04-04 Blower V14
    [Blower V14.f3d, Blower V9.f3d]
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2020-04-05 Fix Blower motor fit
    [Blower V14.f3d, Blower V14.step, Powerhose Fit.stl]
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2020-04-06 Electronics fixes
    [covid-respirator-ProtoB.brd, covid-respirator-ProtoB.sch, respi_V0.fzz]
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2020-04-07 Fix naming issue
    [Pneumatic Connectors V3 - Blower V5.f3d, Pneumatic Connectors V3 - O2 V3.f3d, Pneumatic Connectors V3 - Respiratory No Pressure V2.f3d, Pneumatic Connectors V3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]
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2020-04-07 Fix pneumatic-connector-respiratory-pressure STEP file
    [Pneumatic Connectors V3 - Respiratory Pressure V3.step]
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2020-05-08 Revert "Clear off src/ folder (exported to each sub-repo)"
    This reverts commit 0860ec841f4ae6d55704daa5b23baae60b10e5a0.
    [Adapter 15-15.step, Adapter 15-15.stl, Adapter Validation Compressor Pump 11mm to 15mm.f3d, Adapter Validation Compressor Pump 11mm to 15mm.stl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]
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
